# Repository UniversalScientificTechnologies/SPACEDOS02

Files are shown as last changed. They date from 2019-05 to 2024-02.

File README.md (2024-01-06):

# SPACEDOS02A - PIN diode dosimeter for manned spacecraft 

SPACEDOS is a miniature and lightweight version of [AIRDOS02](https://github.com/UniversalScientificTechnologies/AIRDOS02) cosmic radiation dosimeter modified for use onboard manned spacecraft.

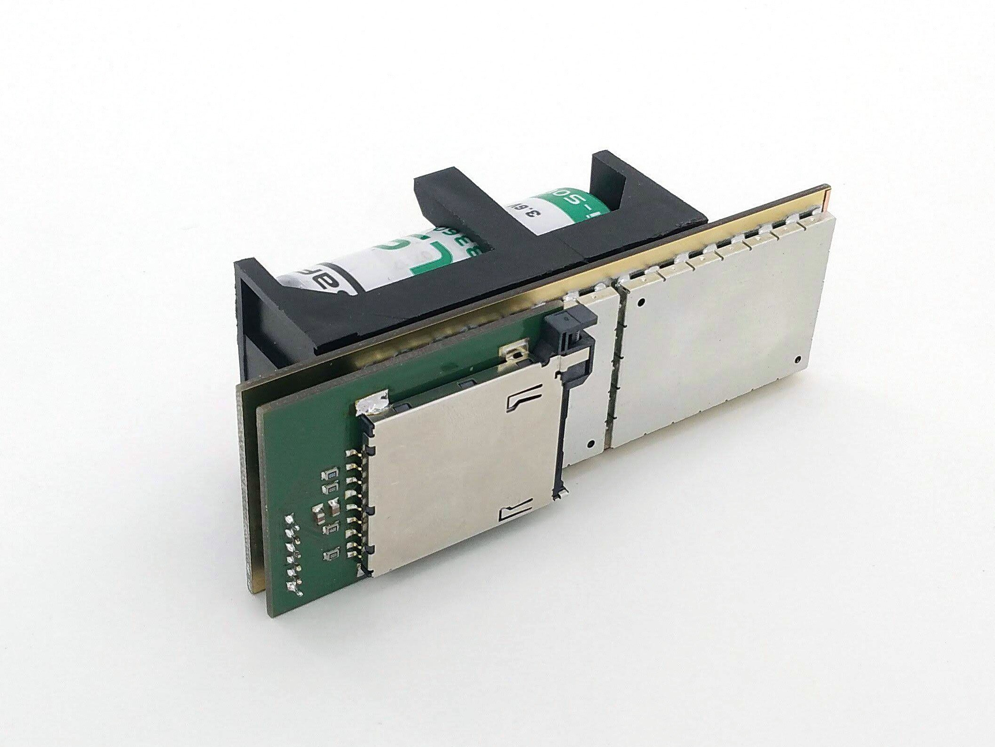
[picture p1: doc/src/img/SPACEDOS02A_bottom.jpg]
SPACEDOS02A device from bottom side PCB

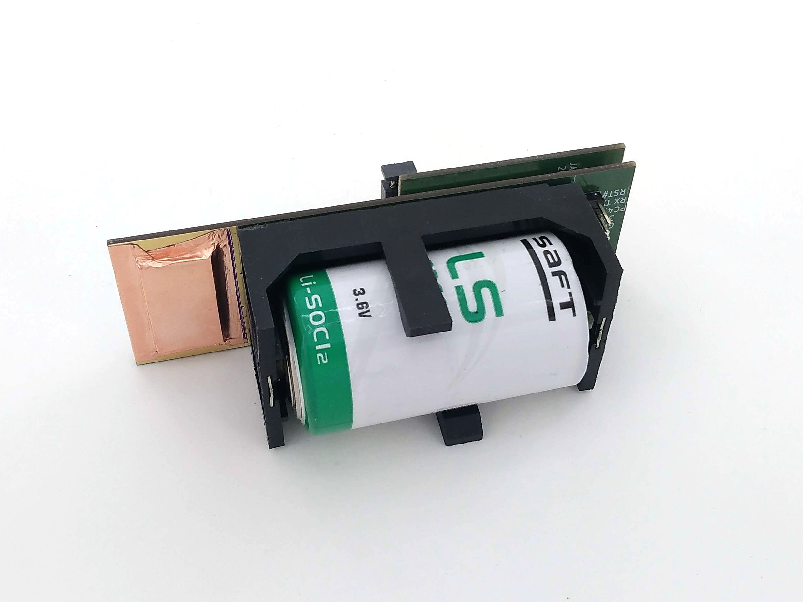
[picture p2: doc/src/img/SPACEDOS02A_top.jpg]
SPACEDOS02A device from top side PCB


The device is currently being used onboard ISS. The following pictures show the processed data from the flight. Here is a radiation map, where the [South Atlantic Anomaly](https://en.wikipedia.org/wiki/South_Atlantic_Anomaly) is visible.

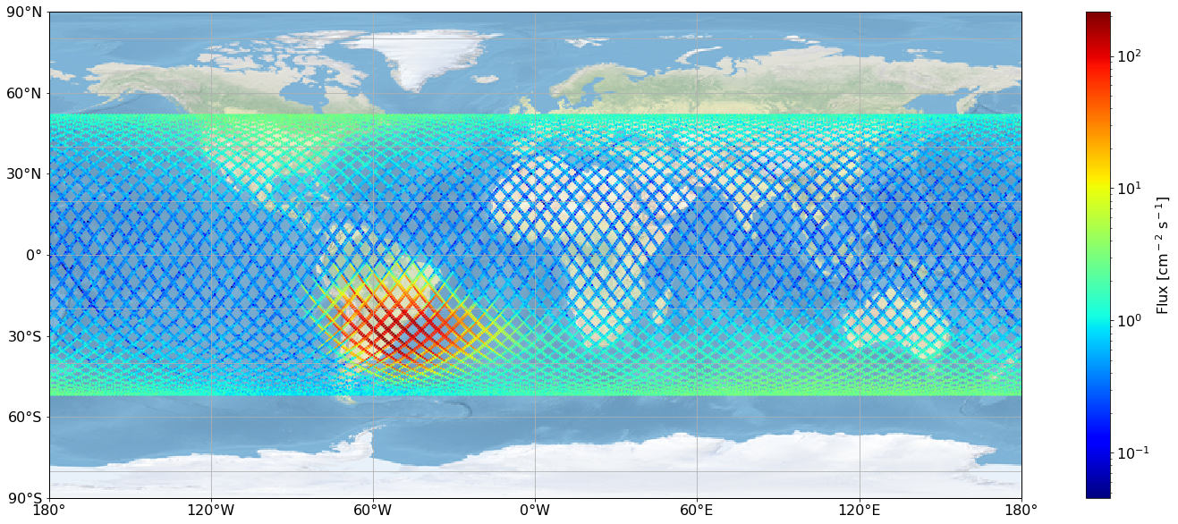
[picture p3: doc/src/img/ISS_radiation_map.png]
ISS radiation map


The following spectrum is a cumulative sum of all the measured particles during the flight. 

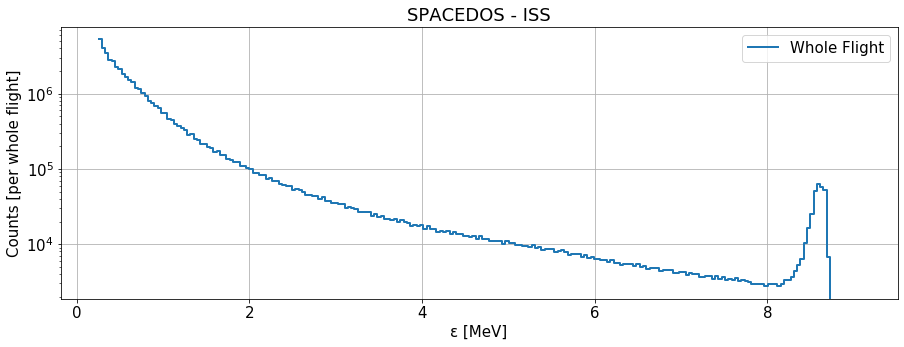
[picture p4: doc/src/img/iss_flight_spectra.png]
ISS radiation spectra


## Technical parameters are as follows:

* Silicon PIN diode detector with 0.22 x 10 x 20 ~ 44 mm³ detection volume
* Measurement environment: atmosphere > 70 kPa
* Measurement endurance: 120 days (4 months of measurement)
* Number of energy channels: 240
* Integration time: Customizable in a wide range from milliseconds to minutes
* Deposited energy range: from 180 keV to 8.5 MeV
* Energy measurement resolution: < 50 keV/channel
* Thermal stability: 1 channel per 12 °C
* Power supply: battery 3.6 V LS 33600
* Power consumption: < 10 mW during measurement, < 120 mW during writing to SD card
* Data storage media: Standard size SDcard, Industry-grade SLC  SD card
* Interface: RS232/UART 3.3V TTL
* Radiation durability: 50 mGy - currently limited by the durability of a storage media
* Dimensions(HxWxL): 60mm x 39mm x 113 mm
* Mass / (including battery): 58/148 g 

## Relevant scientific publications

* [SPACEDOS: AN OPEN-SOURCE PIN DIODE DOSEMETER FOR APPLICATIONS IN SPACE](https://academic.oup.com/rpd/article-abstract/198/9-11/611/6673003?redirectedFrom=fulltext&login=false)
* [SPACEDOS an open-source PIN diode dosimeter for applications in Space](https://indico.ujf.cas.cz/event/2/contributions/27/attachments/25/46/Po-1315-Kakona-774711333.pdf)

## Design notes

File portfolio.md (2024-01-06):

---
title: "Manned spacecraft dosimeter"
excerpt: "SPACEDOS02 is a miniature and lightweight version of [AIRDOS02](https://github.com/UniversalScientificTechnologies/AIRDOS02) dosimeter designed for use on board of manned spacecraft."
header:
  image: products/SPACEDOS02A/doc/src/img/SPACEDOS02A_bottom.jpg
  teaser: products/SPACEDOS02A/doc/src/img/SPACEDOS02A_bottom.jpg
  overlay_color: "#000"
  overlay_filter: "0.5"
  overlay_image: products/SPACEDOS02A/doc/src/img/SPACEDOS02A_bottom.jpg
gallery:
  - image_path: products/SPACEDOS02A/doc/src/img/SPACEDOS02A_bottom.jpg
    alt: "SPACEDOS02A"
  - image_path: products/SPACEDOS02A/doc/src/img/SPACEDOS02A_top.jpg
    alt: "SPACEDOS02A"
  - image_path: products/SPACEDOS02A/doc/src/img/ISS_radiation_map.png
    alt: "Radiation map"
---

{% include gallery %}

SPACEDOS is a miniature and lightweight version of [AIRDOS02](https://github.com/UniversalScientificTechnologies/AIRDOS02) cosmic radiation dosimeter for use on board manned spacecraft.

SPACEDOS02A device from bottom side PCB
SPACEDOS02A device from top side PCB

The device is being used onboard ISS. The following pictures show the processed data from a flight. Here is a radiation map, where the [South Atlantic Anomaly](https://en.wikipedia.org/wiki/South_Atlantic_Anomaly) is visible.

ISS radiation map

The following spectrum is a cumulative sum of all the measured particles during the flight.

ISS radiation spectra

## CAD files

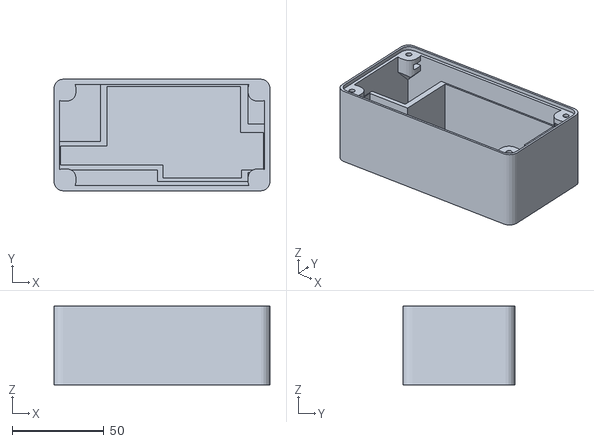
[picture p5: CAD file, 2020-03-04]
hw/CAD/SPACEDOS02A_BASEBOX03A/cad/amf/SPACEDOS02A_BASEBOX03A.stl
118.0 x 61.0 x 43.1

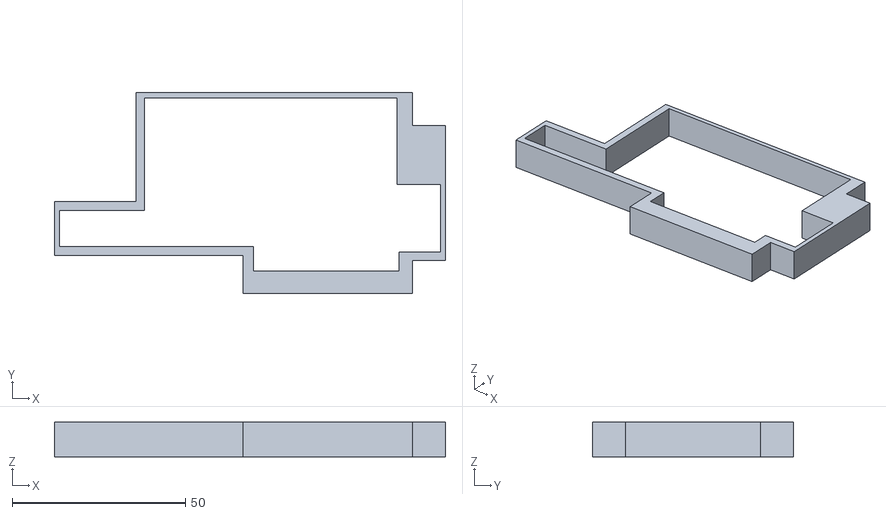
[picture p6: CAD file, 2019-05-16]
hw/CAD/SPACEDOS02A_CAD01A.stl
113.0 x 58.0 x 10.0

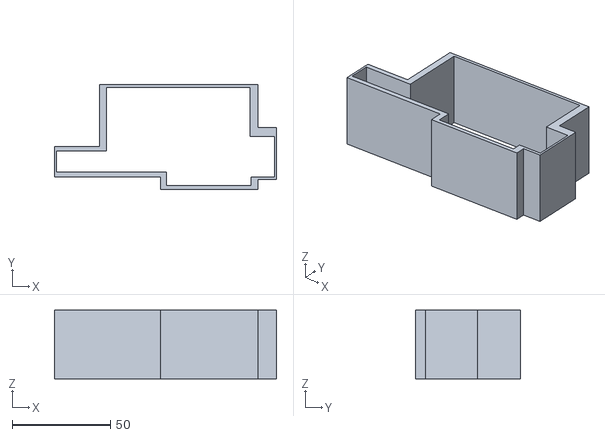
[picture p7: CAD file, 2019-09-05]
hw/CAD/SPACEDOS02A_CAD01A/amf/SPACEDOS02A_CAD01A.stl
113.0 x 53.5 x 35.0

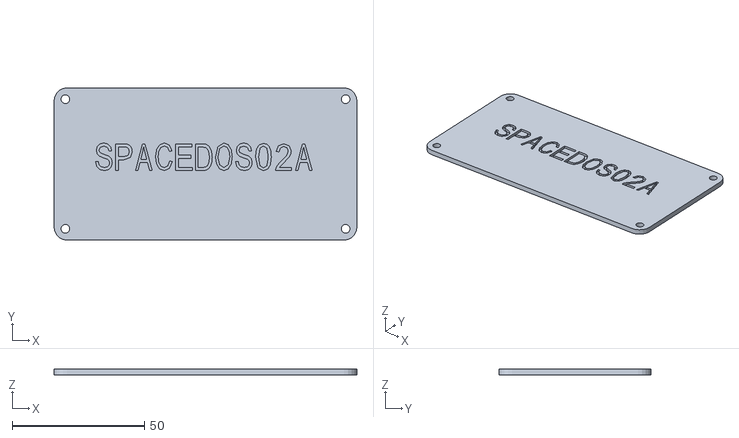
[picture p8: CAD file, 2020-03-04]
hw/CAD/SPACEDOS02A_BASEBOX03A/cad/amf/SPACEDOS02A_BASEBOX03A_PLBASE_top.stl
114.6 x 57.6 x 2.10

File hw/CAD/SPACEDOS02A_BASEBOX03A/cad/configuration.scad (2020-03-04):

//Název boxu (zařízení)
box_jmeno="SPACEDOS02A";

vzdalenost_der = 1; //rozteč děr mezi sebou
radidus_hrany = 5; //radius zaobleni sloupku
vzdalenost_od_okraje = 8.2; //vzdalenost stredu upevnovaci diry od kraje desky
vzdalenost_od_okraje1 = 0;
vzdalenost_od_okraje2 = 0;
pocet_der1 = 56; //pocet děr v ose y
pocet_der2 = 113; //pocet der v ose x



//OBECNE PARAMETRY KRABICKY
//------------------------------------------------------------
//BOCNICE
vyska_bocnice=39;
tloustka_bocnice=3;


//PLBASE PARAMETRY
//------------------------------------------------------------
tloustka_plbase = 2; //tloustka plbase - dna
prekryti_der=0.2; //sila materiálu, který překrývá díry, aby nebyli vidět

plbase_tolerance_horni=0.5; //pro zvětšení tolerance aby tam šlo dát  horní čelíčko


//Rozmery loga MLAB
//------------------------------------------------------------
logo_vyska=0.15;
logo_sirka=0.15;


//Sroub M3
M3_prumer=3.4;
M3_prumer_hlavy=7;
M3_vyska_hlavy=5;
M3_vyska_matky=3;
M3_sirka_matky=6.7;
Uchyt_vyska_mat=4;
Uchyt_radius=2;
Uchyt_x=13;
Uchyt_y=10;

dno_vyska_ramecku=9;
dno_vule=0.6;
dno_sila_materialu=4;
dno_spodni_rantl=3;
dno_vule_na_matky=0;

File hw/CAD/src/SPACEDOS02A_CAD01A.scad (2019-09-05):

//Rozmery kovové krabicky vnitrni
krabicka_x=113;
krabicka_y=58;
krabicka_z=35;  //35

krabicka_otvor_hrana=9.5;

//Rozmery casty modulu
pcb_x=111;
pcb_y=6;

baterka_x=73;
baterka_y=37;

konektor_x=12.5;
konektor_y=12;

SD_karta_x=43;
SD_karta_y=13;

SD_karta_mensi_x=12;
SD_karta_mensi_y=8.5;

dioda_x=25.5;
dioda_y=4.5;

SPACEDOS02A_CAD01A();

module SPACEDOS02A_CAD01A()
    {
    difference(){

        KRABICKA();
            translate([1,19.5,-0.5]) 
                MODUL();    
                } 
    }


module KRABICKA()
    {
    difference(){
        cube([krabicka_x,krabicka_y,krabicka_z],center=false);

//otvory
        translate([0,0,-0.5]) 
            cube([krabicka_otvor_hrana,krabicka_otvor_hrana,krabicka_z+1],center=false);
    
        translate([krabicka_x-krabicka_otvor_hrana,0,-0.5]) 
            cube([krabicka_otvor_hrana,krabicka_otvor_hrana,krabicka_z+1],center=false);
        
        translate([0,krabicka_y-krabicka_otvor_hrana,-0.5]) 
            cube([krabicka_otvor_hrana,krabicka_otvor_hrana,krabicka_z+1],center=false);
    
        translate([krabicka_x-krabicka_otvor_hrana,krabicka_y-krabicka_otvor_hrana-12-0.5]) 
            cube([krabicka_otvor_hrana,krabicka_otvor_hrana+20,krabicka_z+1],center=false);


                }
    }   


module MODUL()
    {

    //pcb
    translate([0,-pcb_y,-0.5]) 
        cube([pcb_x,pcb_y,krabicka_z+1],center=false);

    //konektor
    translate([pcb_x-konektor_x,0,-0.5]) 
        cube([konektor_x,konektor_y,krabicka_z+1],center=false);

    //baterka
    translate([pcb_x-konektor_x-baterka_x,0,-0.5]) 
        cube([baterka_x,baterka_y,krabicka_z+1],center=false);

    //dioda
    translate([pcb_x-konektor_x-baterka_x-dioda_x,0,-0.5]) 
        cube([dioda_x,dioda_y,krabicka_z+1],center=false);

    //SD karta
    translate([pcb_x-SD_karta_x-SD_karta_mensi_x,-SD_karta_y,-0.5]) 
        cube([SD_karta_x,SD_karta_y,krabicka_z+1],center=false);
        
    //SD karta mensi otvor
    translate([pcb_x-SD_karta_mensi_x,-SD_karta_mensi_y,-0.5]) 
        cube([SD_karta_mensi_x,SD_karta_mensi_y,krabicka_z+1],center=false);  
     
    //vyrez levy horni
    translate([-2,7,-0.5]) 
       cube([24,60,krabicka_z+1],center=false);  
        
         //vyrez levy dolni
    translate([-2,-21,-0.5]) 
        cube([55,12.5,krabicka_z+1],center=false);  
     
   //vyrez pravy dolni
    translate([-2,-21,-0.5]) 
        cube([krabicka_x+4,6,krabicka_z+1],center=false);     
        
       //vyrez pravy horni
    translate([-2,7,-0.5]) 
       cube([24,60,krabicka_z+1],center=false);    
    
     }

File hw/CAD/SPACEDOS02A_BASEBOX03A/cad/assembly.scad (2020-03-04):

use <src/sloupek.scad>
use <src/plbase.scad>
use <src/bocnice.scad>
use <src/dno.scad>
use <src/spodni_kryt.scad>
use <src/otvory.scad>
use <src/text/Write.scad>
use <upravena_bocnice.scad>

include <src/manufactury_conf.scad>
include <configuration.scad>
include <src/otvory_conf.scad>


barva_dno_bocnice = "cyan";
barva_spodni_kryt = "green";
barva_plbase_horni = "yellow";

posuv_dilu=10; //pro složeni krabičky zadat 0 pro rozebrání zdat 10

//BOCNICE SE DNEM
//-------------------------------------------------------------


translate([0,0,-2*posuv_dilu])
translate([-((pocet_der2-1)*vzdalenost_der+2*vzdalenost_od_okraje2)/2-tloustka_bocnice,-vzdalenost_od_okraje1-tloustka_bocnice,-(vyska_bocnice/2)-tloustka_plbase])
        rotate(a=[180,0,90])

plbase_bez_der2(pocet_der1,pocet_der2,radidus_hrany,vzdalenost_der,vzdalenost_od_okraje1,vzdalenost_od_okraje2,prumer_sroubu,tloustka_plbase,prekryti_der,tloustka_bocnice);


color(barva_dno_bocnice)
    upravena_bocnice();

//PLBASE HORNI
//-------------------------------------------------------------
translate([0,0,5*posuv_dilu])
color(barva_plbase_horni)
translate([0,0,vyska_bocnice/2-tloustka_plbase/2])
    rotate(a=[0,0,0])
        {
  
     plbase_vrchni_kryt_pro_odecet(pocet_der1-1,pocet_der2-1,radidus_hrany,vzdalenost_der,vzdalenost_od_okraje1,vzdalenost_od_okraje2,prumer_sroubu,vyska_bocnice,prekryti_der,tloustka_bocnice,plbase_tolerance_horni,tloustka_plbase);    
     }

//SPODNÍ KRYT
//-------------------------------------------------------------
/*
translate([0,0,-5*posuv_dilu])
color(barva_spodni_kryt)
translate([0,0,-vyska_bocnice/2-2*tloustka_plbase])
    spodni_kryt(pocet_der1-1,pocet_der2-1,radidus_hrany,vzdalenost_der,vzdalenost_od_okraje,prumer_sroubu,vyska_bocnice,prekryti_der,tloustka_bocnice);

*/


/*
translate([0,0,-5*posuv_dilu])
color(barva_spodni_kryt)
translate([0,0,-tloustka_plbase-dno_sila_materialu])
   dno(pocet_der1-1,pocet_der2-1,radidus_hrany,vzdalenost_der,vzdalenost_od_okraje1,vzdalenost_od_okraje2,prumer_sroubu,vyska_bocnice,prekryti_der,tloustka_bocnice);
*/

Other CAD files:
hw/CAD/SPACEDOS02A_BASEBOX03A/cad/upravena_bocnice.scad
hw/CAD/SPACEDOS02A_BASEBOX03A/cad/print_data/SPACEDOS02A_BASEBOX03A.scad
hw/CAD/SPACEDOS02A_BASEBOX03A/cad/print_data/SPACEDOS02A_BASEBOX03A_PLBASE_top.scad
hw/CAD/SPACEDOS02A_BASEBOX03A/cad/src/MLAB_logo.scad
hw/CAD/SPACEDOS02A_BASEBOX03A/cad/src/bocnice.scad
hw/CAD/SPACEDOS02A_BASEBOX03A/cad/src/dno.scad
hw/CAD/SPACEDOS02A_BASEBOX03A/cad/src/manufactury_conf.scad
hw/CAD/SPACEDOS02A_BASEBOX03A/cad/src/otvory.scad
hw/CAD/SPACEDOS02A_BASEBOX03A/cad/src/otvory_conf.scad
hw/CAD/SPACEDOS02A_BASEBOX03A/cad/src/plbase.scad
hw/CAD/SPACEDOS02A_BASEBOX03A/cad/src/produkt_logo.scad
hw/CAD/SPACEDOS02A_BASEBOX03A/cad/src/sloupek.scad
hw/CAD/SPACEDOS02A_BASEBOX03A/cad/src/spodni_kryt.scad
hw/CAD/SPACEDOS02A_BASEBOX03A/cad/src/text/Write.scad
hw/CAD/SPACEDOS02A_CAD01A/print_data/P_SPACEDOS02A_CAD01A.scad
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

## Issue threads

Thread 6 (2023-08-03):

### ISSUE TITLE
TFPayload connector

### ISSUE THREAD

**Issue by kaklik** [UniversalScientificTechnologies/SPACEDOS02#6]
Pro použití v UAV je potřeba přidat ještě [konektor pro připojení TFGPS](https://github.com/ThunderFly-aerospace/TFGPS01#payload-conector). Ideálně obdobně, jako je vyřešeno na THUNDERMILL.

**Comment by ChroustJan** [comment]
@kaklik prosím blíže specifikovat. Nechápu význam tohoto konektoru. Proč by měla jít GPS přes SPACEDOS. GPS by měla jít do TF-UNIPAYLOAD

**Comment by roman-dvorak** [comment]
Jde především o to, aby spacedos znal přesný čas a podle něj (například) předával naměřená data dále (do autopilota).


Měl by tam jít přípojit 8 pinový konektor z GPS pro payload:

![obrazek](https://user-images.githubusercontent.com/5196729/147094763-9303b797-921b-4630-bbdd-aadfeec913b6.png)

**Comment by kaklik** [comment]
> @kaklik prosím blíže specifikovat. Nechápu význam tohoto konektoru. Proč by měla jít GPS přes SPACEDOS. GPS by měla jít do TF-UNIPAYLOAD

V případě použití SPACEDOSu je přece TFUNIPAYLOAD ten stejný procesor jako je ve SPACEDOS.   Je to stejná situace jako THUNDERMILL.

Ten konektor je logické přidat na SPACEDOS i z toho důvodu, že je pravděpodobné, že SPADEDOS potažmo AIRDOS se budou v některých případech používat samostatně v kombinaci s GPS přijímačem. 

Bližší specifikaci toho konektoru dal Roman v tabulce výše. Její originální zdroj je ale [tady](https://github.com/ThunderFly-aerospace/TFGPS01#payload-conector).

**Comment by ChroustJan** [comment]
@kaklik v případě použití THUNDERMILL tam budou dvě GPS? Neměla by být jedna v TFUNIPAYLOAD a ostatní si ty data spíš brát? Nebo lépe řečeno TFUNIPAYLOAD přidávat časovou značku ke všem záznamům?

**Comment by ChroustJan** [comment]
@kaklik potřebuji definovat propojení konektoru s procesorem, aby bylo možné zvážit, jak moc velká je to komplikace:
![image](https://user-images.githubusercontent.com/9783606/147346039-3fcdff1f-ce32-4328-9d0e-fd56a5e05ac9.png)

Procesor:
![image](https://user-images.githubusercontent.com/9783606/147346091-7784064a-0e74-4927-9004-dec6e932e623.png)

**Comment by kaklik** [comment]
> @kaklik v případě použití THUNDERMILL tam budou dvě GPS? Neměla by být jedna v TFUNIPAYLOAD a ostatní si ty data spíš brát? Nebo lépe řečeno TFUNIPAYLOAD přidávat časovou značku ke všem záznamům?

Já nerozumím tomu na co se ptáš. Jde ti o situaci, kdy bude na UAV víc snímačů najednou? Například THUNDERMILL a AIRDOS zároveň? 

Přidání časové značky k záznamům má obecný problém, že časová značka musí být přidávána co nejblíže k měřeným datům, jinak se ztrácí její význam. Nerozumím proto tomu, jak by vložení další desky (TFUNIPAYLOAD) do systému zlepšilo situaci. 

Pokud ti ale jde o tu situaci více měřících zařízení využívajících TFGPS zároveň, tak zde jsme omezeni počtem UART portů, které autopilot má. V takovém případě pak až do naplnění tohoto omezeného počtu snímačů, se domnívám že, TFPayload konektor na TFGPS stačí pouze elektricky rozdělit do více vodičů. Nejspíše sletováním více vodičů k sobě. Profesionálnější řešení by asi bylo na to navrhout PCB.

**Comment by kaklik** [comment]
> @kaklik potřebuji definovat propojení konektoru s procesorem, aby bylo možné zvážit, jak moc velká je to komplikace: ![image]

Tak zapojení by se hodilo zachovat co největší míře stejné jako to je v případě [THUNDERMILL](https://github.com/mlab-modules/USTTHUNDERMILLPCB01/blob/1f451887b65ddf556598e68d01f601bc215d85c5/hw/sch_pcb/USTTHUNDERMILLPCB01A/USTTHUNDERMILLPCB01A.pdf) tj. takhle: 

![image](https://user-images.githubusercontent.com/1194177/147369047-6e7bab07-d364-4c57-8b2d-9cc29f773e7f.png)

U pinů, u kterých to není možné, tak ty je nutné přesunout na nějaké jiné volné a na PCB zapojitelné piny na MCU. Myslím že konkrétně jde akorát o piny GEO_STAT a EXTINT, které zrovna mohou být zapojeny asi na jakýkoliv pin.

**Comment by kaklik** [comment]
Tato úprava je realizována v [USTSIPIN02A](https://github.com/ust-modules/USTSIPIN02), který tím pokrývá tento use case.

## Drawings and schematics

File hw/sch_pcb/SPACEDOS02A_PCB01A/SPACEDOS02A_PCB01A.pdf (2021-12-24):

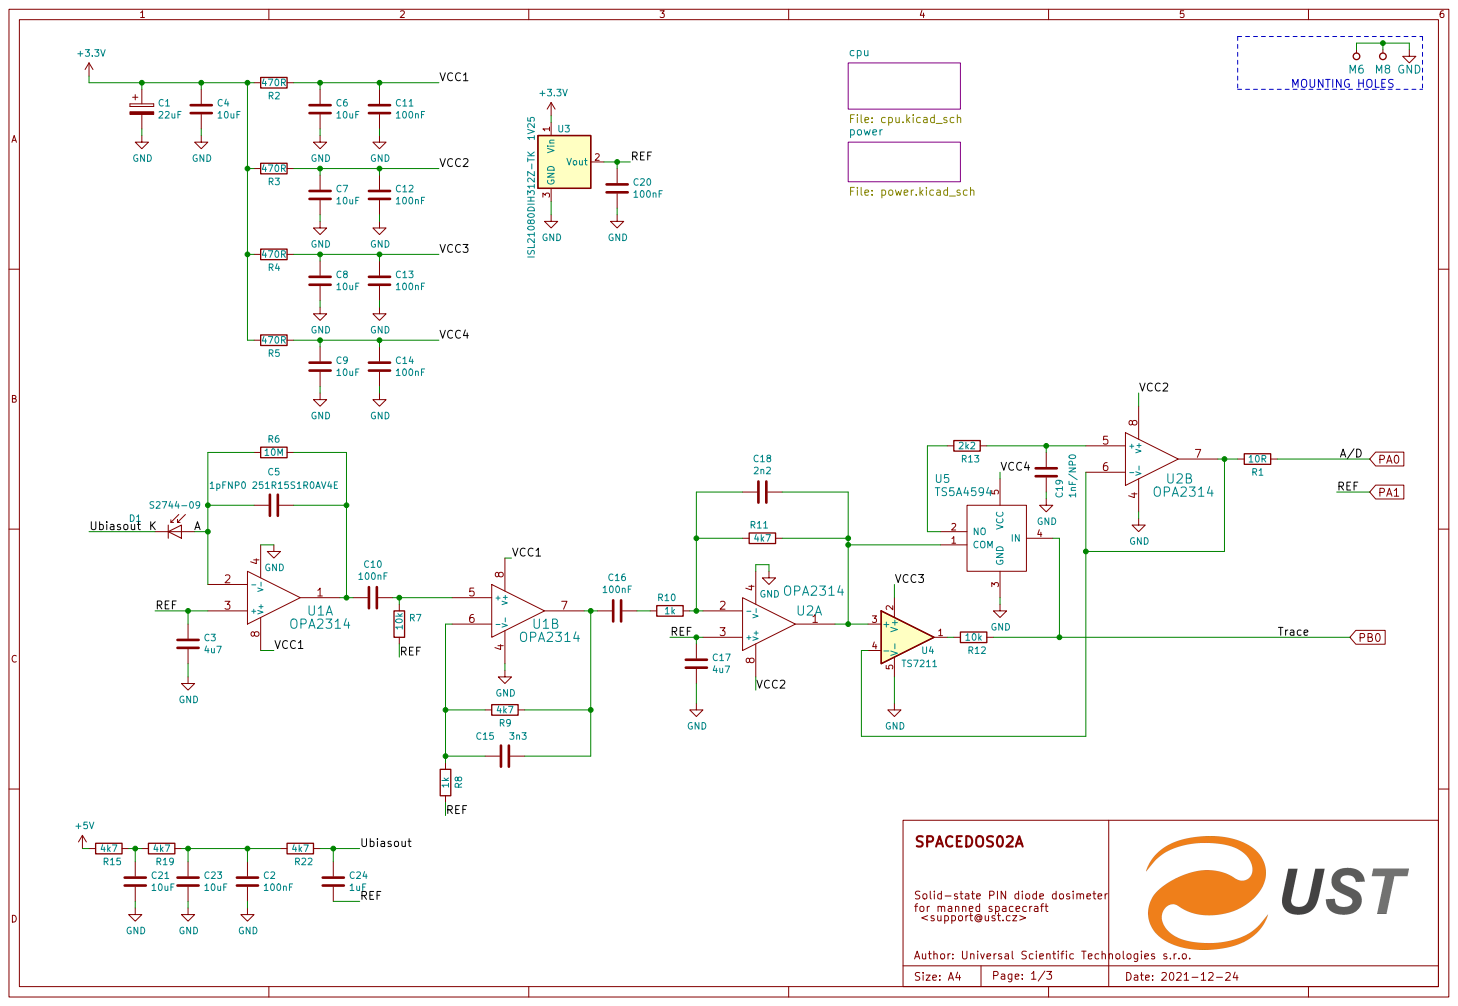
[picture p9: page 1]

Solid-state PIN diode dosimeter
<support@ust.cz>

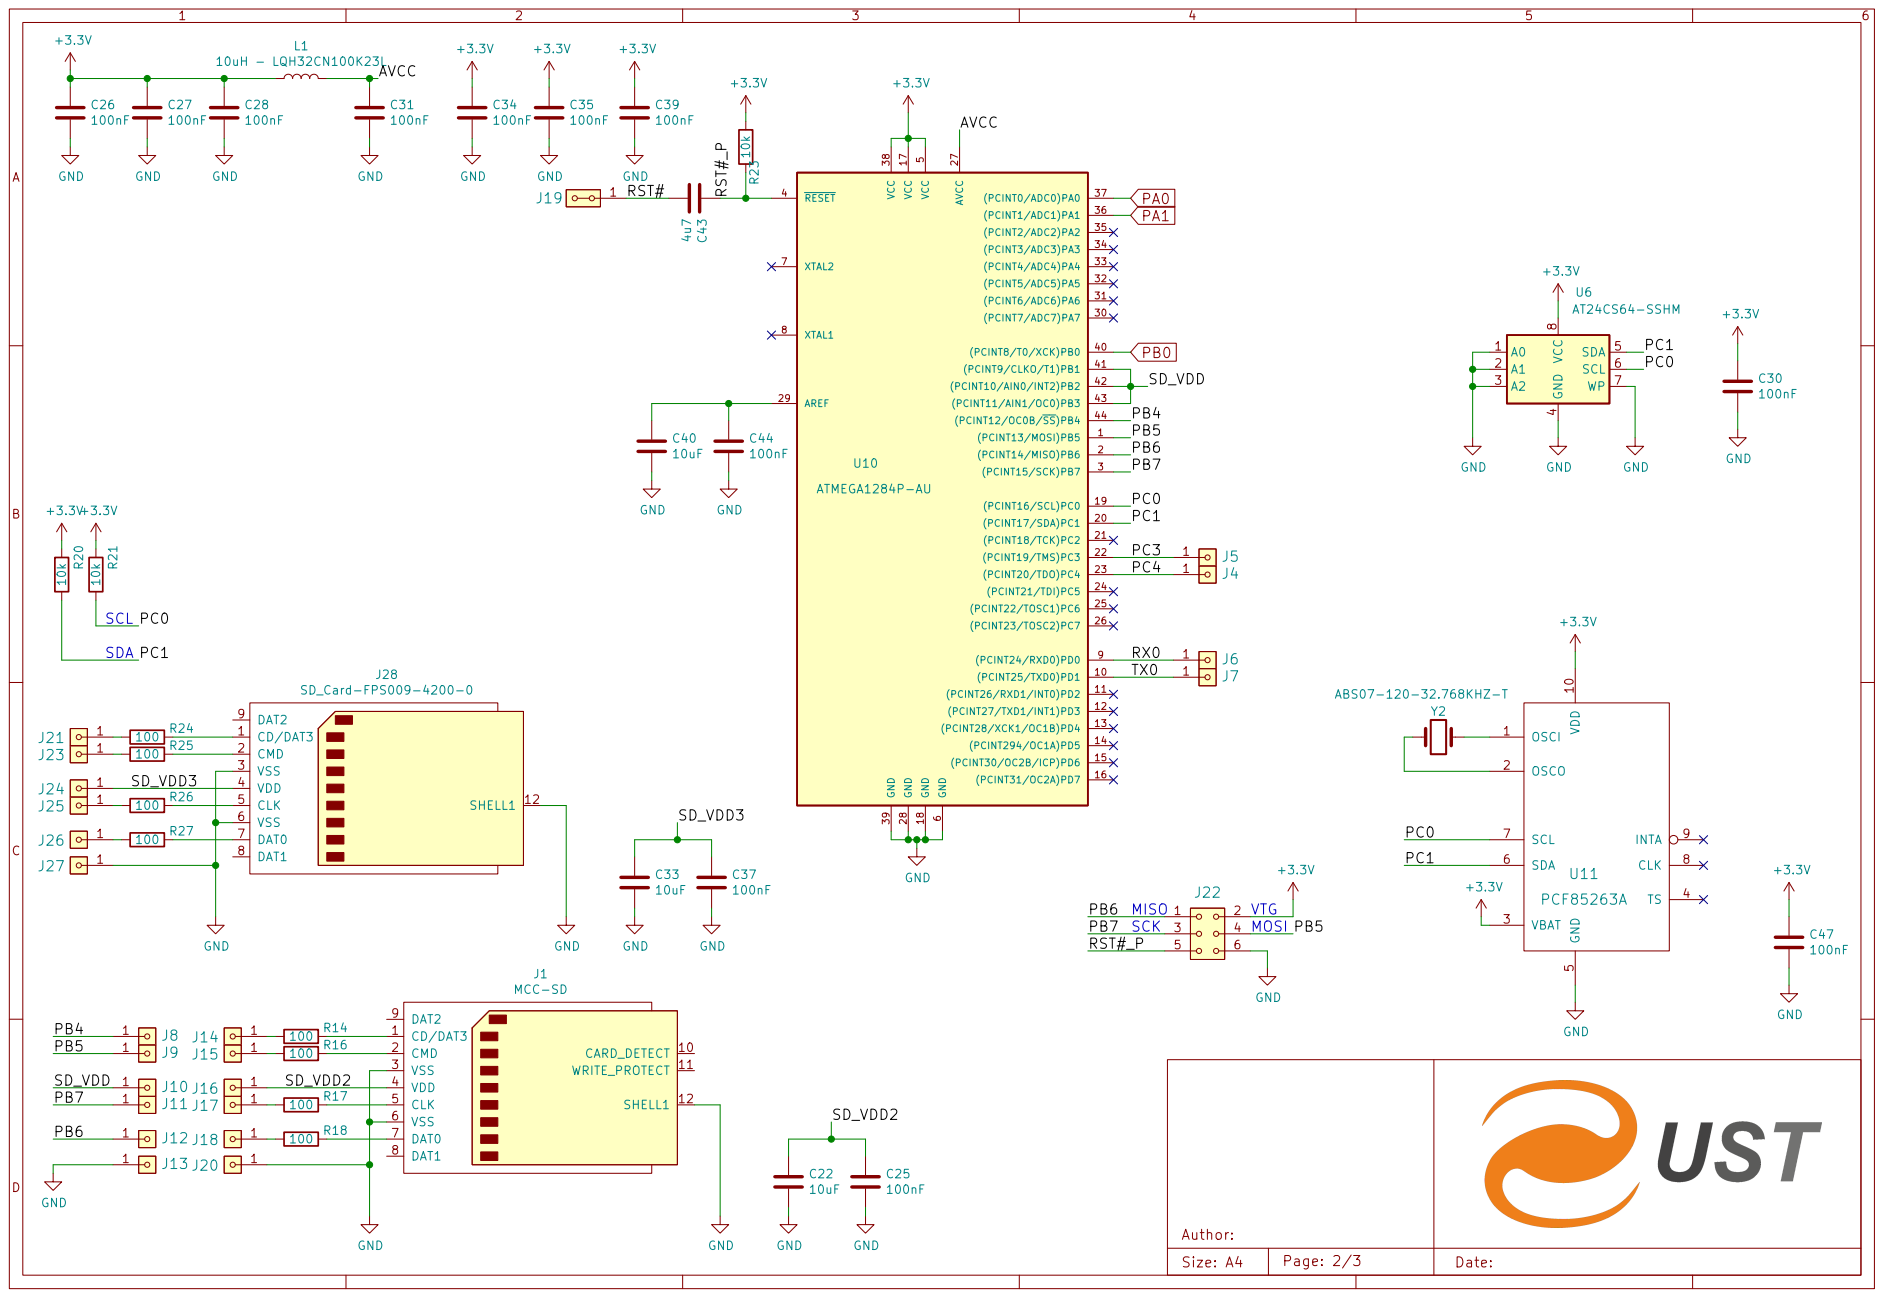
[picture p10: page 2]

4 SDA 5 SCL 6 WP 7 VCC

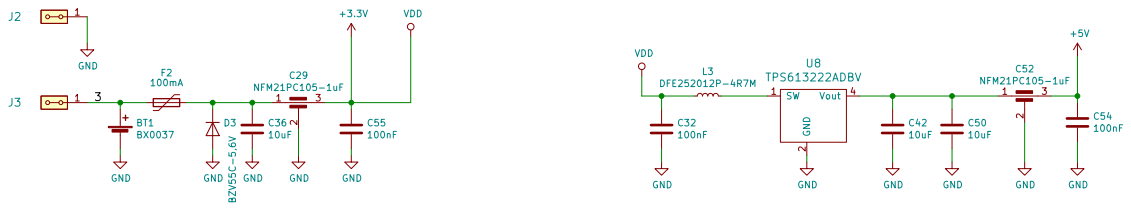
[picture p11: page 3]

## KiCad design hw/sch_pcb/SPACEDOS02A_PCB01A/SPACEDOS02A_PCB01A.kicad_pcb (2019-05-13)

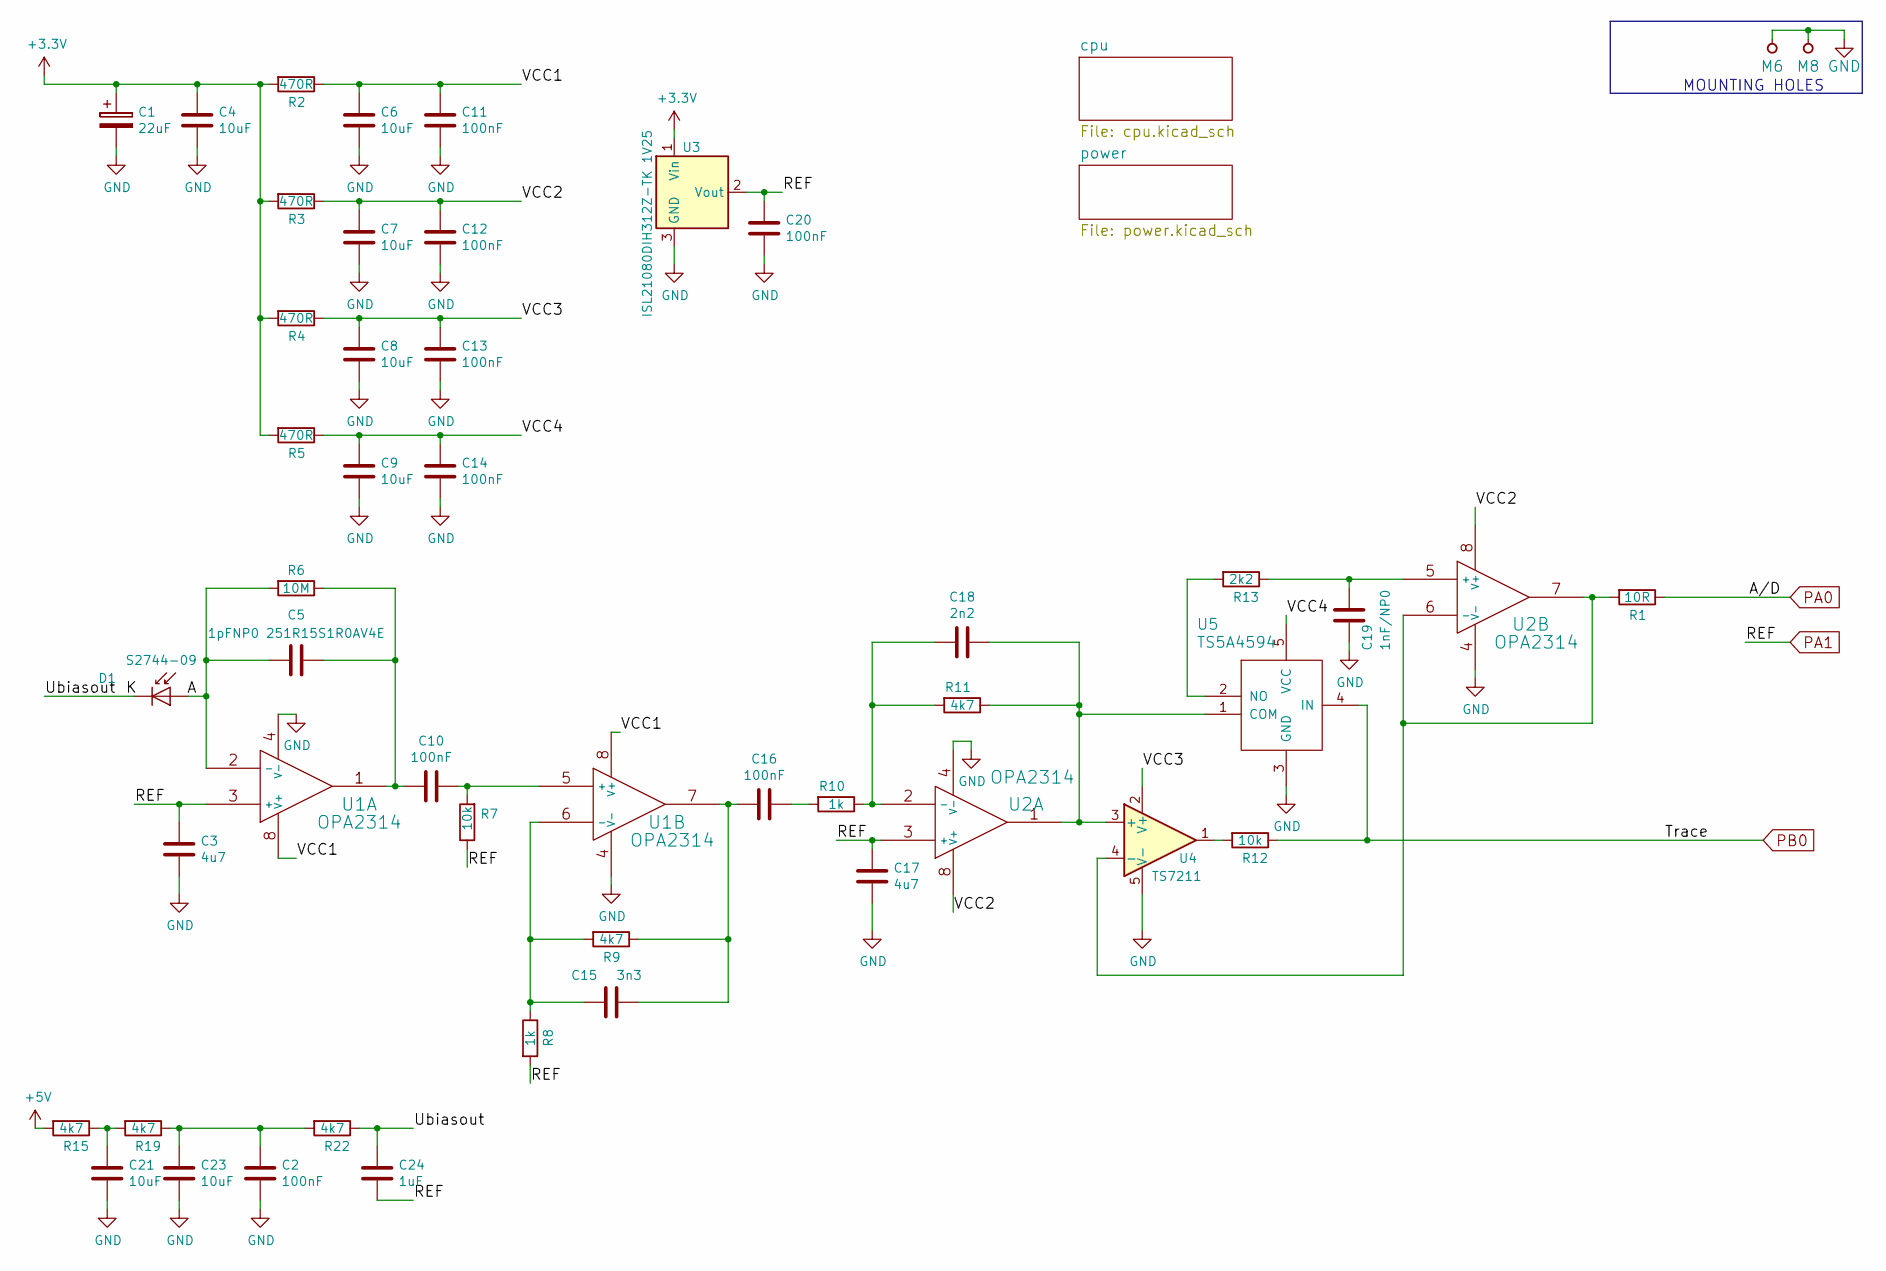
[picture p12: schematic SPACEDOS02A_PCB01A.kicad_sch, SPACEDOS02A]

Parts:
C1: 22uF; TantalC_SizeC_Reflow
C2, C10, C11, C12, C13, C14, C16, C20: 100nF; SMD-0805
C3, C17: 4u7; SMD-0805
C4, C6, C7, C8, C9, C21, C23: 10uF; SMD-0805
C5: 1pFNP0 251R15S1R0AV4E; SMD-0805
C15: 3n3; SMD-0805
C18: 2n2; SMD-0805
C19: 1nF/NP0; SMD-0805
C24: 1uF; SMD-0805
D1: S2744-09; HAMAMATSU_S2744-09
M6: BMI-S-210-F
M8: BMI-S-210-F; Laird_Technologies_BMI-S-210-F_44.00x30.50mm
R1: 10R; SMD-0805
R2, R3, R4, R5: 470R; SMD-0805
R6: 10M; SMD-0805
R7, R12: 10k; SMD-0805
R8, R10: 1k; SMD-0805
R9, R11, R15, R19, R22: 4k7; SMD-0805
R13: 2k2; SMD-0805
U1, U2: OPA2314; SOIC-8_3.9x4.9mm_Pitch1.27mm
U3: ISL21080DIH312Z-TK 1V25; SOT-23
U4: TS7211; SOT-23-5_HandSoldering
U5: TS5A4594; SOT-23-5_HandSoldering

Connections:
+3V3: C1.1, C4.1, R2.2, R3.2, R4.2, R5.2, U3.1 (Vin); also elsewhere on the board
+5V: R15.2; also elsewhere on the board
/A: C5.2, D1.2 (A), R6.2, U1.2 (-)
/K: C24.1, D1.1 (K), R22.1
/VCC1: C6.1, C11.1, R2.1, U1.8 (V+)
/VCC2: C7.1, C12.1, R3.1, U2.8 (V+)
/VCC3: C8.1, C13.1, R4.1, U4.2 (V+)
/VCC4: C9.1, C14.1, R5.1, U5.5 (VCC)
GND: C1.2, C2.2, C3.2, C4.2, C6.2, C7.2, C8.2, C9.2, C11.2, C12.2, C13.2, C14.2, C17.2, C19.2, C20.2, C21.2, C23.2, M6.1, M8.1, U1.4 (V-), U2.4 (V-), U3.3 (GND), U4.5 (V-), U5.3 (GND); also elsewhere on the board
unnamed: C2.1, C23.1, R19.1, R22.2
unnamed: C10.1, R7.2, U1.5 (+)
unnamed: C5.1, C10.2, R6.1, U1.1
unnamed: C15.1, C16.2, R9.1, U1.7
unnamed: C15.2, R8.1, R9.2, U1.6 (-)
unnamed: C16.1, R10.2
unnamed: C18.1, R11.1, U2.1, U4.3 (+), U5.1 (COM)
unnamed: C18.2, R10.1, R11.2, U2.2 (-)
unnamed: C19.1, R13.1, U2.5 (+)
unnamed: C21.1, R15.1, R19.2
unnamed: R1.2, U2.6 (-), U2.7, U4.4 (-)
unnamed: R12.2, U4.1
unnamed: R13.2, U5.2 (NO)
PA0: R1.1; also elsewhere on the board
PA1: C3.1, C17.1, C20.1, C24.2, R7.1, R8.2, U1.3 (+), U2.3 (+), U3.2 (Vout); also elsewhere on the board
PB0: R12.1, U5.4 (IN); also elsewhere on the board

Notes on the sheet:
MOUNTING HOLES

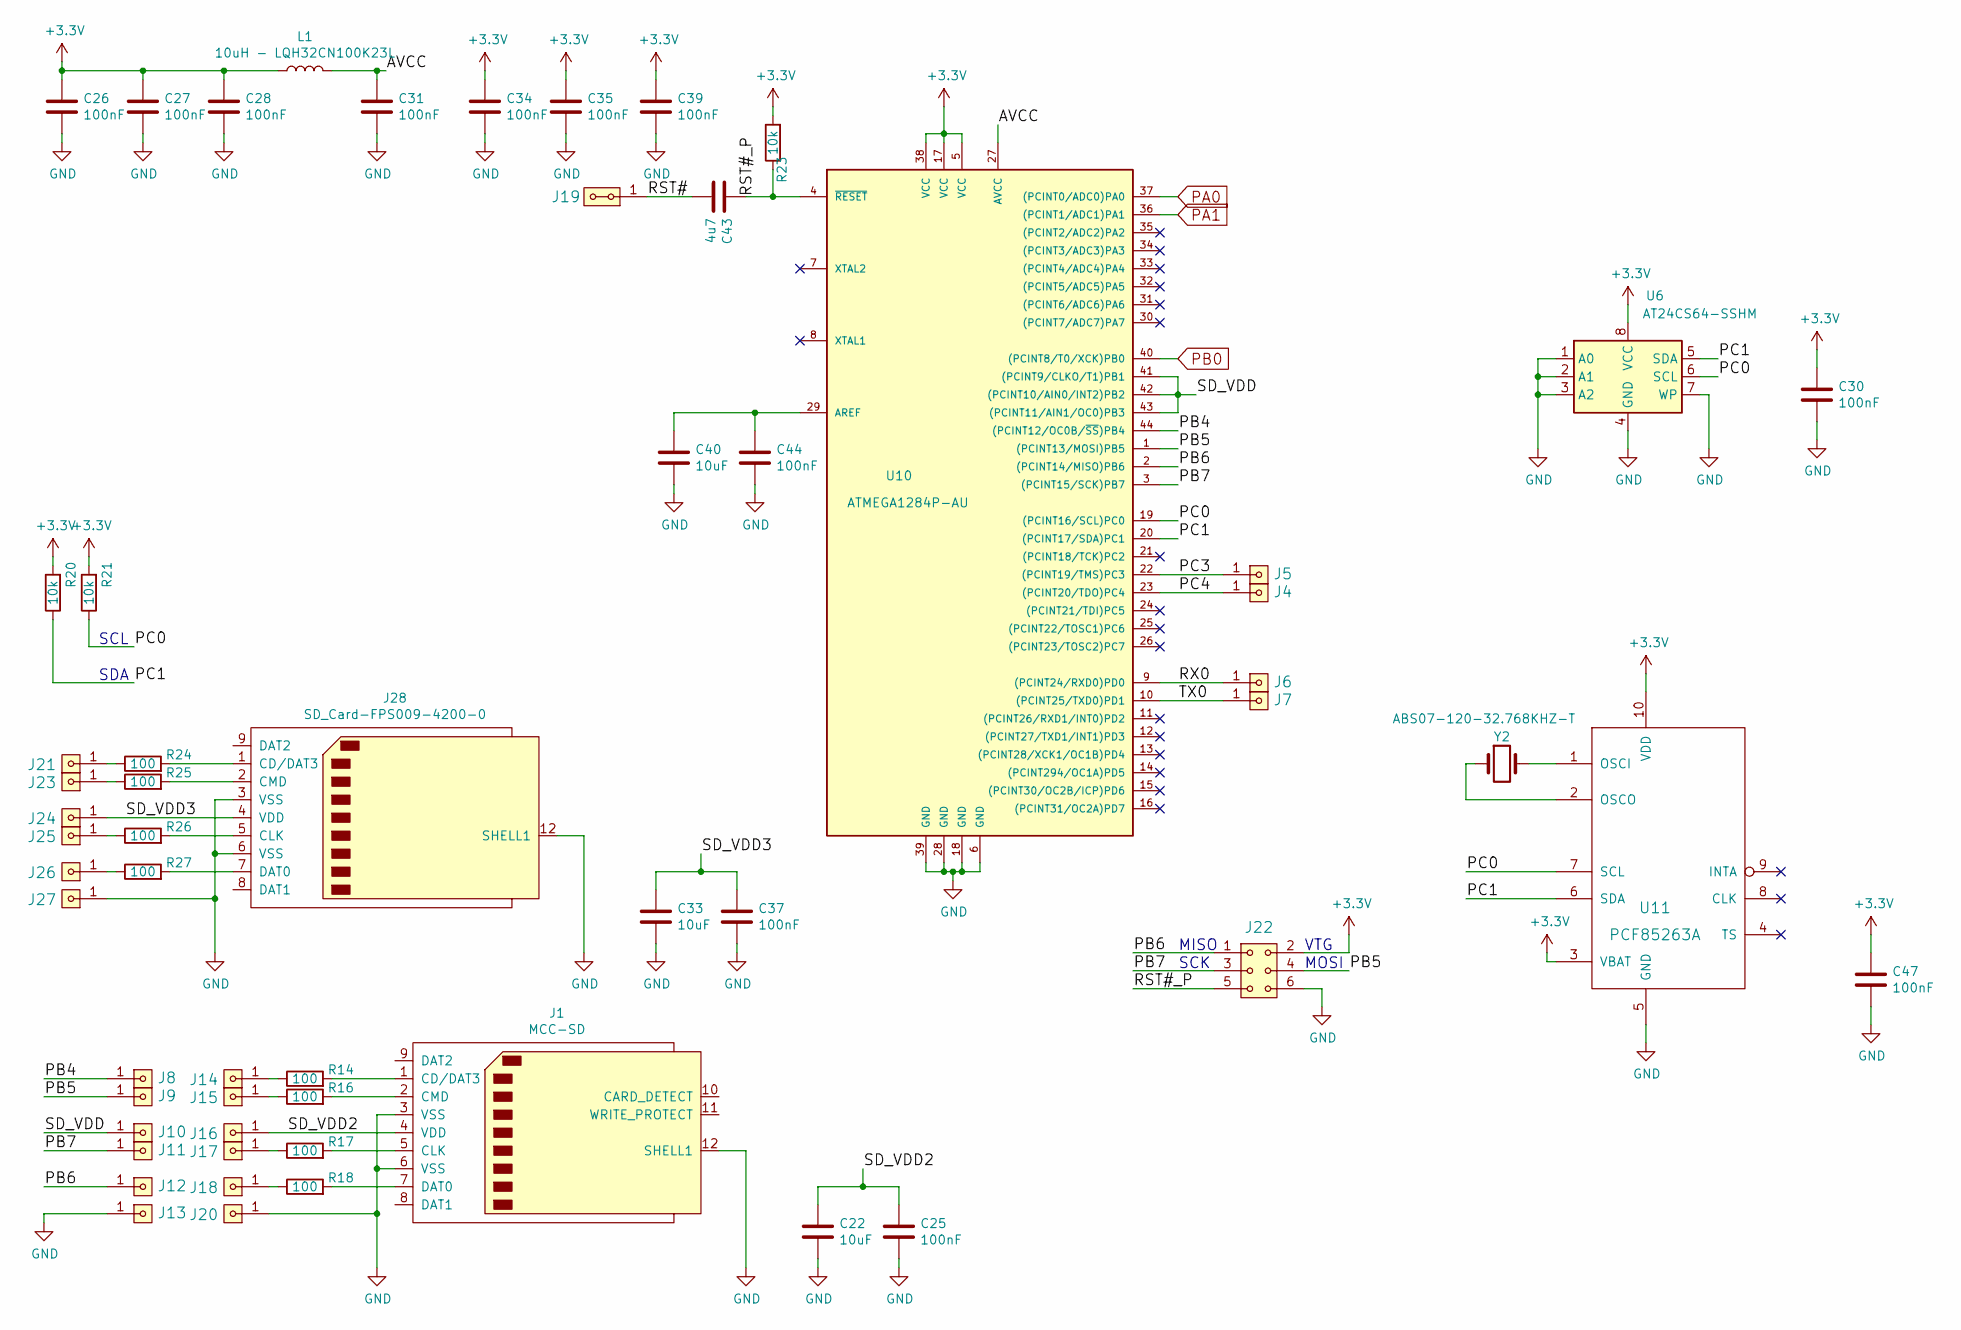
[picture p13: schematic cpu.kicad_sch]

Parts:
C22, C33, C40: 10uF; SMD-0805
C25, C26, C27, C28, C30, C31, C34, C35, C37, C39, C44, C47: 100nF; SMD-0805
C43: 4u7; SMD-0805
J1: MCC-SD
J4, J5, J6, J7, J8, J9, J10, J11, J12, J13, J14, J15, J16, J17, J18, J20, J21, J23, J24, J25, J26, J27: HEADER_1x01; Straight_1x01
J19: HEADER_2x01_PARALLEL; Straight_2x01
J22: HEADER_2x03; SMD_2x03
J28: SD_Card-FPS009-4200-0; FPS009-4200-0
L1: 10uH - LQH32CN100K23L; SMD-1210
R14, R16, R17, R18, R24, R25, R26, R27: 100; SMD-0805
R20, R21, R23: 10k; SMD-0805
U6: AT24CS64-SSHM; SOIC-8_3.9x4.9mm_P1.27mm
U10: ATMEGA1284P-AU; TQFP-44_10x10mm_P0.8mm
U11: PCF85263A; TSSOP-10_3x3mm_Pitch0.5mm
Y2: ABS07-120-32.768KHZ-T; ABS07

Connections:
+3V3: C26.1, C27.1, C28.1, C30.1, C34.1, C35.1, C39.1, C47.1, J22.2, L1.1, R20.2, R21.2, R23.2, U6.8 (VCC), U10.5 (VCC), U10.17 (VCC), U10.38 (VCC), U11.3 (VBAT), U11.10 (VDD); also elsewhere on the board
/cpu/AVCC: C31.1, L1.2, U10.27 (AVCC)
/cpu/PB4: J8.1, U10.44 ((PCINT12/OC0B/~SS)PB4)
/cpu/PB5: J9.1, J22.4, U10.1 ((PCINT13/MOSI)PB5)
/cpu/PB6: J12.1, J22.1, U10.2 ((PCINT14/MISO)PB6)
/cpu/PB7: J11.1, J22.3, U10.3 ((PCINT15/SCK)PB7)
/cpu/PC0: R21.1, U6.6 (SCL), U10.19 ((PCINT16/SCL)PC0), U11.7 (SCL)
/cpu/PC1: R20.1, U6.5 (SDA), U10.20 ((PCINT17/SDA)PC1), U11.6 (SDA)
/cpu/PC3: J5.1, U10.22 ((PCINT19/TMS)PC3)
/cpu/PC4: J4.1, U10.23 ((PCINT20/TDO)PC4)
/cpu/RST#: C43.2, J19.1, J19.2
/cpu/RST#_P: C43.1, J22.5, R23.1, U10.4 (~RESET)
/cpu/RX0: J6.1, U10.9 ((PCINT24/RXD0)PD0)
/cpu/SD_VDD: J10.1, U10.41 ((PCINT9/CLKO/T1)PB1), U10.42 ((PCINT10/AIN0/INT2)PB2), U10.43 ((PCINT11/AIN1/OC0)PB3)
/cpu/SD_VDD2: C22.1, C25.1, J1.4 (VDD), J16.1
/cpu/SD_VDD3: C33.1, C37.1, J24.1, J28.4 (VDD)
/cpu/TX0: J7.1, U10.10 ((PCINT25/TXD0)PD1)
GND: C22.2, C25.2, C26.2, C27.2, C28.2, C30.2, C31.2, C33.2, C34.2, C35.2, C37.2, C39.2, C40.2, C44.2, C47.2, J1.3 (VSS), J1.6 (VSS), J1.12 (SHELL1), J13.1, J20.1, J22.6, J27.1, J28.3 (VSS), J28.6 (VSS), J28.12 (SHELL1), U6.1 (A0), U6.2 (A1), U6.3 (A2), U6.4 (GND), U6.7 (WP), U10.6 (GND), U10.18 (GND), U10.28 (GND), U10.39 (GND), U11.5 (GND); also elsewhere on the board
unnamed: C40.1, C44.1, U10.29 (AREF)
unnamed: J1.1 (CD/DAT3), R14.2
unnamed: J1.2 (CMD), R16.2
unnamed: J1.5 (CLK), R17.2
unnamed: J1.7 (DAT0), R18.2
unnamed: J14.1, R14.1
unnamed: J15.1, R16.1
unnamed: J17.1, R17.1
unnamed: J18.1, R18.1
unnamed: J21.1, R24.1
unnamed: J23.1, R25.1
unnamed: J25.1, R26.1
unnamed: J26.1, R27.1
unnamed: J28.1 (CD/DAT3), R24.2
unnamed: J28.2 (CMD), R25.2
unnamed: J28.5 (CLK), R26.2
unnamed: J28.7 (DAT0), R27.2
unnamed: U11.1 (OSCI), Y2.2
unnamed: U11.2 (OSCO), Y2.1
PA0: U10.37 ((PCINT0/ADC0)PA0); also elsewhere on the board
PA1: U10.36 ((PCINT1/ADC1)PA1); also elsewhere on the board
PB0: U10.40 ((PCINT8/T0/XCK)PB0); also elsewhere on the board

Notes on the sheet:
MOSI
SCK
MISO
VTG
SDA
SCL

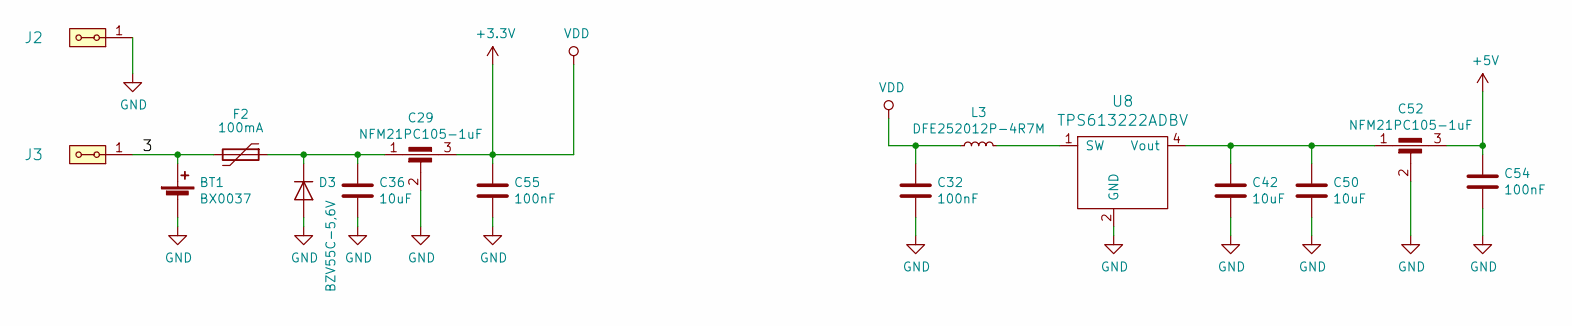
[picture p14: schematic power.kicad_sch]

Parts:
BT1: BX0037; BX0037_nez_sroubu
C29, C52: NFM21PC105-1uF; FIR_0805
C32, C54, C55: 100nF; SMD-0805
C36, C42, C50: 10uF; SMD-0805
D3: BZV55C-5,6V; D_MiniMELF
F2: 100mA; SMD-0805
J2, J3: HEADER_2x01_PARALLEL; Straight_1x02
L3: DFE252012P-4R7M; R_0805_2012Metric_Pad1.15x1.40mm_HandSolder
U8: TPS613222ADBV; SOT-23-5

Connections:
+3V3: C29.3, C32.1, C55.1, L3.1; also elsewhere on the board
+5V: C52.3, C54.1; also elsewhere on the board
/power/3: BT1.1 (+), F2.2, J3.1, J3.2
GND: BT1.2 (-), C29.2, C32.2, C36.2, C42.2, C50.2, C52.2, C54.2, C55.2, D3.2 (A), J2.1, J2.2, U8.2 (GND); also elsewhere on the board
unnamed: C29.1, C36.1, D3.1 (K), F2.1
unnamed: C42.1, C50.1, C52.1, U8.4 (Vout)
unnamed: L3.2, U8.1 (SW)

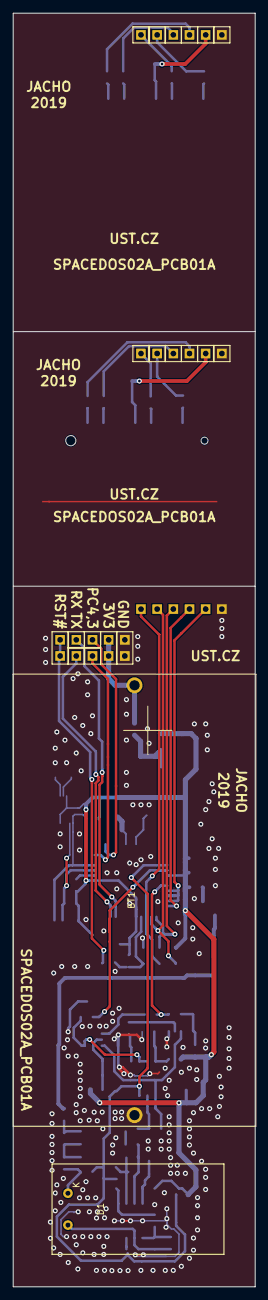
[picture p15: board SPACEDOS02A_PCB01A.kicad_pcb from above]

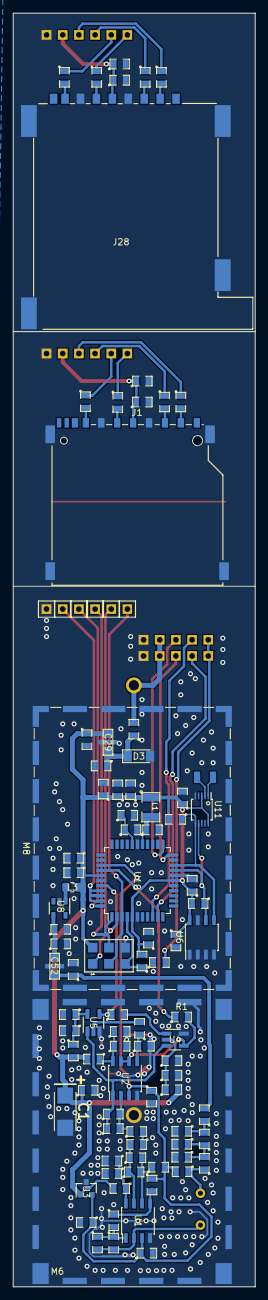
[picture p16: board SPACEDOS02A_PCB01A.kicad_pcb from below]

Board: 2 copper layers, 38.0 x 200.0 mm, 120 parts (99 on the bottom side), 64 nets.

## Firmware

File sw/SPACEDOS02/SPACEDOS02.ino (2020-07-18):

String githash = "808689c";
String FWversion = "S01";
#define LAUNCH  30+30+14+12 // Number of days to launch
#define ZERO 260  // 1st channel without noise

/*
  SPACEDOS with RTC (AIRDOS-F with reduced number of channels)
 
ISP
---
PD0     RX
PD1     TX
RESET#  through 50M capacitor to RST#

SDcard
------
DAT3   SS   4 B4
CMD    MOSI 5 B5
DAT0   MISO 6 B6
CLK    SCK  7 B7

ANALOG
------
+      A0  PA0
-      A1  PA1
RESET  0   PB0

LED
---
LED_yellow  23  PC7         // LED for Dasa (not connected in SPACEDOS)

Startup Delay
-------------
JUMPER  19 PC3    // Selection of delayed start
                  // H = Delayed start
                  // L = Immediate start

                     Mighty 1284p    
                      +---\/---+
           (D 0) PB0 1|        |40 PA0 (AI 0 / D24)
           (D 1) PB1 2|        |39 PA1 (AI 1 / D25)
      INT2 (D 2) PB2 3|        |38 PA2 (AI 2 / D26)
       PWM (D 3) PB3 4|        |37 PA3 (AI 3 / D27)
    PWM/SS (D 4) PB4 5|        |36 PA4 (AI 4 / D28)
      MOSI (D 5) PB5 6|        |35 PA5 (AI 5 / D29)
  PWM/MISO (D 6) PB6 7|        |34 PA6 (AI 6 / D30)
   PWM/SCK (D 7) PB7 8|        |33 PA7 (AI 7 / D31)
                 RST 9|        |32 AREF
                VCC 10|        |31 GND
                GND 11|        |30 AVCC
              XTAL2 12|        |29 PC7 (D 23)
              XTAL1 13|        |28 PC6 (D 22)
      RX0 (D 8) PD0 14|        |27 PC5 (D 21) TDI
      TX0 (D 9) PD1 15|        |26 PC4 (D 20) TDO
RX1/INT0 (D 10) PD2 16|        |25 PC3 (D 19) TMS
TX1/INT1 (D 11) PD3 17|        |24 PC2 (D 18) TCK
     PWM (D 12) PD4 18|        |23 PC1 (D 17) SDA
     PWM (D 13) PD5 19|        |22 PC0 (D 16) SCL
     PWM (D 14) PD6 20|        |21 PD7 (D 15) PWM
                      +--------+
*/

/*
// Compiled with: Arduino 1.8.9
// MightyCore 2.0.2 https://mcudude.github.io/MightyCore/package_MCUdude_MightyCore_index.json
Fix old bug in Mighty SD library
~/.arduino15/packages/MightyCore/hardware/avr/2.0.2/libraries/SD/src/SD.cpp:
boolean SDClass::begin(uint32_t clock, uint8_t csPin) {
  if(root.isOpen()) root.close();
*/

#include <SD.h>             // Revised version from MightyCore
#include "wiring_private.h"
#include <Wire.h>           
#include "src/RTCx/RTCx.h"  // Modified version included

#define LED_yellow  23   // PC7
#define RESET       0    // PB0
#define SDpower1    1    // PB1
#define SDpower2    2    // PB2
#define SDpower3    3    // PB3
#define SS          4    // PB4
#define MOSI        5    // PB5
#define MISO        6    // PB6
#define SCK         7    // PB7
#define INT         20   // PC4
#define JUMPER      19   // PC3

#define CHANNELS 512 // number of channels in buffer for histogram, including negative numbers

uint16_t count = 0;
uint32_t serialhash = 0;
uint16_t offset;
uint16_t base_offset = ZERO - 1;
uint8_t lo, hi;
uint16_t u_sensor, maximum;
struct RTCx::tm tm;

// Read Analog Differential without gain (please read datashet of ATMega1280 and ATMega2560 for refference)
// Use analogReadDiff(NUM)
//   NUM  | POS PIN             | NEG PIN           |   GAIN
//  0 | A0      | A1      | 1x
//  1 | A1      | A1      | 1x
//  2 | A2      | A1      | 1x
//  3 | A3      | A1      | 1x
//  4 | A4      | A1      | 1x
//  5 | A5      | A1      | 1x
//  6 | A6      | A1      | 1x
//  7 | A7      | A1      | 1x
//  8 | A8      | A9      | 1x
//  9 | A9      | A9      | 1x
//  10  | A10     | A9      | 1x
//  11  | A11     | A9      | 1x
//  12  | A12     | A9      | 1x
//  13  | A13     | A9      | 1x
//  14  | A14     | A9      | 1x
//  15  | A15     | A9      | 1x
#define PIN 0
uint8_t analog_reference = INTERNAL2V56; // DEFAULT, INTERNAL, INTERNAL1V1, INTERNAL2V56, or EXTERNAL

void setup()
{

  // Open serial communications and wait for port to open:
  Serial.begin(9600);

  Serial.println("#Cvak...");
  
  ADMUX = (analog_reference << 6) | ((PIN | 0x10) & 0x1F);
  
  ADCSRB = 0;               // Switching ADC to Free Running mode
  sbi(ADCSRA, ADATE);       // ADC autotrigger enable (mandatory for free running mode)
  sbi(ADCSRA, ADSC);        // ADC start the first conversions
  sbi(ADCSRA, 2);           // 0x100 = clock divided by 16, 62.5 kHz, 208 us for 13 cycles of one AD conversion, 24 us fo 1.5 cycle for sample-hold
  cbi(ADCSRA, 1);        
  cbi(ADCSRA, 0);        

  pinMode(RESET, OUTPUT);   // reset for peak detetor

  //pinMode(SDpower1, OUTPUT);  // SDcard interface
  //pinMode(SDpower2, OUTPUT);     
  //pinMode(SDpower3, OUTPUT);     
  //pinMode(SS, OUTPUT);     
  //pinMode(MOSI, INPUT);     
  //pinMode(MISO, INPUT);     
  //pinMode(SCK, OUTPUT);  

  DDRB = 0b10011110;
  PORTB = 0b00000000;  // SDcard Power OFF

  DDRA = 0b11111100;
  PORTA = 0b00000000;  // SDcard Power OFF
  DDRC = 0b11110100;
  PORTC = 0b00000000;  // SDcard Power OFF
  DDRD = 0b11111100;
  PORTD = 0b00000000;  // SDcard Power OFF

  pinMode(LED_yellow, OUTPUT);
  digitalWrite(LED_yellow, LOW);  
  digitalWrite(RESET, LOW);  
  
  Wire.setClock(100000);
  // Initiates RTC
  rtc.autoprobe();
  rtc.resetClock();

  for(int i=0; i<5; i++)  
  {
    delay(50);
    digitalWrite(LED_yellow, HIGH);  // Blink for Dasa 
    delay(50);
    digitalWrite(LED_yellow, LOW);  
  }

  Serial.println("#Hmmm...");

  // make a string for device identification output
  String dataString = "$AIRDOS," + FWversion + "," + String(ZERO) + "," + githash + ","; // FW version and Git hash
  
  Wire.beginTransmission(0x58);                   // request SN from EEPROM
  Wire.write((int)0x08); // MSB
  Wire.write((int)0x00); // LSB
  Wire.endTransmission();
  Wire.requestFrom((uint8_t)0x58, (uint8_t)16);    
  for (int8_t reg=0; reg<16; reg++)
  { 
    uint8_t serialbyte = Wire.read(); // receive a byte
    if (serialbyte<0x10) dataString += "0";
    dataString += String(serialbyte,HEX);    
    serialhash += serialbyte;
  }

  {
    DDRB = 0b10111110;
    PORTB = 0b00001111;  // SDcard Power ON
  
    // make sure that the default chip select pin is set to output
    // see if the card is present and can be initialized:
    if (!SD.begin(SS)) 
    {
      Serial.println("#Card failed, or not present");
      // don't do anything more:
      return;
    }
  
    // open the file. note that only one file can be open at a time,
    // so you have to close this one before opening another.
    File dataFile = SD.open("datalog.txt", FILE_WRITE);
  
    // if the file is available, write to it:
    if (dataFile) 
    {
      dataFile.println(dataString);  // write to SDcard (800 ms)     
      dataFile.close();
  
      digitalWrite(LED_yellow, HIGH);  // Blink for Dasa
      Serial.println(dataString);  // print SN to terminal 
      digitalWrite(LED_yellow, LOW);          
    }  
    // if the file isn't open, pop up an error:
    else 
    {
      Serial.println("#error opening datalog.txt");
    }
  
    DDRB = 0b10011110;
    PORTB = 0b00000001;  // SDcard Power OFF          
  }    

  // measurement of ADC offset
  ADMUX = (analog_reference << 6) | 0b10001; // Select +A1,-A1 for offset correction
  delay(200);
  ADCSRB = 0;               // Switching ADC to Free Running mode
  sbi(ADCSRA, ADATE);       // ADC autotrigger enable (mandatory for free running mode)
  sbi(ADCSRA, ADSC);        // ADC start the first conversions
  sbi(ADCSRA, 2);           // 0x100 = clock divided by 16, 62.5 kHz, 208 us for 13 cycles of one AD conversion, 24 us fo 1.5 cycle for sample-hold
  cbi(ADCSRA, 1);
  cbi(ADCSRA, 0);
  sbi(ADCSRA, ADIF);                  // reset interrupt flag from ADC
  while (bit_is_clear(ADCSRA, ADIF)); // wait for the first conversion
  sbi(ADCSRA, ADIF);                  // reset interrupt flag from ADC
  lo = ADCL;
  hi = ADCH;
  ADMUX = (analog_reference << 6) | 0b10000; // Select +A0,-A1 for measurement
  ADCSRB = 0;               // Switching ADC to Free Running mode
  sbi(ADCSRA, ADATE);       // ADC autotrigger enable (mandatory for free running mode)
  sbi(ADCSRA, ADSC);        // ADC start the first conversions
  sbi(ADCSRA, 2);           // 0x100 = clock divided by 16, 62.5 kHz, 208 us for 13 cycles of one AD conversion, 24 us fo 1.5 cycle for sample-hold
  cbi(ADCSRA, 1);
  cbi(ADCSRA, 0);
  // combine the two bytes
  u_sensor = (hi << 7) | (lo >> 1);
  // manage negative values
  if (u_sensor <= (CHANNELS / 2) - 1 ) {
    u_sensor += (CHANNELS / 2);
  } else {
    u_sensor -= (CHANNELS / 2);
  }

  {
    rtc.readClock(tm);
    RTCx::time_t t = RTCx::mktime(&tm);
  
    dataString = "$TIME,";
    dataString += String(t-946684800);  // RTC Time of the power-on

    DDRB = 0b10111110;
    PORTB = 0b00001111;  // SDcard Power ON
  
    // make sure that the default chip select pin is set to output
    // see if the card is present and can be initialized:
    if (!SD.begin(SS)) 
    {
      Serial.println("#Card failed, or not present");
      // don't do anything more:
      return;
    }
  
    // open the file. note that only one file can be open at a time,
    // so you have to close this one before opening another.
    File dataFile = SD.open("datalog.txt", FILE_WRITE);
  
    // if the file is available, write to it:
    if (dataFile) 
    {
      dataFile.println(dataString);  // write to SDcard (800 ms)     
      dataFile.close();
  
      digitalWrite(LED_yellow, HIGH);  // Blink for Dasa
      Serial.println(dataString);  // print to terminal 
      digitalWrite(LED_yellow, LOW);          
    }  
    // if the file isn't open, pop up an error:
    else 
    {
      Serial.println("#error opening datalog.txt");
    }
  
    DDRB = 0b10011110;
    PORTB = 0b00000001;  // SDcard Power OFF          
  }    

  // disable power of peripherials
  disablePower(POWER_ADC);
  disablePower(POWER_SPI);
  disablePower(POWER_WIRE);
  disablePower(POWER_SERIAL1);
  disablePower(POWER_TIMER1);
  disablePower(POWER_TIMER2);
  disablePower(POWER_TIMER3);

  // waiting for launch
  if (digitalRead(JUMPER)==HIGH)
  {
    // H = Delayed start
   for(uint8_t n=0; n<(LAUNCH); n++) 
      delay(1000ul*60ul*60ul*24ul); // waiting one day    
  }
  else
  {
    // L = Immediate start
    for(uint8_t n=0; n<(1); n++) 
      delay(1000ul*10ul); // waiting a while    
  }
  
  // enable power of peripherials
  enablePower(POWER_ADC);
  enablePower(POWER_SPI);
  enablePower(POWER_WIRE);

  {
    rtc.readClock(tm);
    RTCx::time_t t = RTCx::mktime(&tm);
  
    dataString = "$TIME,";
    dataString += String(t-946684800);  // RTC Time of the launch

    DDRB = 0b10111110;
    PORTB = 0b00001111;  // SDcard Power ON
  
    // make sure that the default chip select pin is set to output
    // see if the card is present and can be initialized:
    if (!SD.begin(SS)) 
    {
      Serial.println("#Card failed, or not present");
      // don't do anything more:
    }
  
    // open the file. note that only one file can be open at a time,
    // so you have to close this one before opening another.
    File dataFile = SD.open("datalog.txt", FILE_WRITE);
  
    // if the file is available, write to it:
    if (dataFile) 
    {
      dataFile.println(dataString);  // write to SDcard (800 ms)     
      dataFile.close();
  
      digitalWrite(LED_yellow, HIGH);  // Blink for Dasa
      Serial.println(dataString);  // print SN to terminal 
      digitalWrite(LED_yellow, LOW);          
    }  
    // if the file isn't open, pop up an error:
    else 
    {
      Serial.println("#error opening datalog.txt");
    }
  
    DDRB = 0b10011110;
    PORTB = 0b00000001;  // SDcard Power OFF          
  }

  disablePower(POWER_SPI);
  disablePower(POWER_WIRE);
}
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

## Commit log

2019-04-26 Edit PCB
    [SPACEDOS02A_PCB01A.kicad_pcb, SPACEDOS02A_PCB01A.sch, cpu.sch, power.sch]
2019-05-16 Box holder
    [SPACEDOS02A_CAD01A.scad]
2019-05-16 zmena vykresu
    [SPACEDOS02A_CAD01A.scad, SPACEDOS02A_CAD01A.stl]
2019-05-17 uklid, nove parametry
    [P_SPACEDOS02A_CAD01A.scad, SPACEDOS02A_CAD01A.scad, SPACEDOS02A_CAD01A.stl]
2019-05-19 Zmena modelu
    [SPACEDOS02A_CAD01A.scad, SPACEDOS02A_CAD01A.stl]
2020-03-04 Tvorba krabicky
    [Letters.dxf, MLAB_logo.scad, P_SPACEDOS02A_CAD01A.scad, SPACEDOS02A_BASEBOX03A.scad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]
2021-12-24 Updated title block updated version of kicad used.
    [SPACEDOS02A_PCB01A.kicad_sch, SPACEDOS02A_PCB01A.sch, cpu.kicad_sch, cpu.sch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]

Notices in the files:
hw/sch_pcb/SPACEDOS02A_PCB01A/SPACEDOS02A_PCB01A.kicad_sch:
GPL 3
